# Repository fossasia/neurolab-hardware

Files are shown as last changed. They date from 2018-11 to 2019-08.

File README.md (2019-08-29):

# Neurolab Hardware

Repository for Neurolab Open Hardware platform.






We are developing a neuro-device to collect brainwaves as a headband with integrated electronics. This repository holds the PCB schematics and layouts for the Neurolab Hardware. 

Front Side               | Back Side
 ----------------------- | ---------------------------
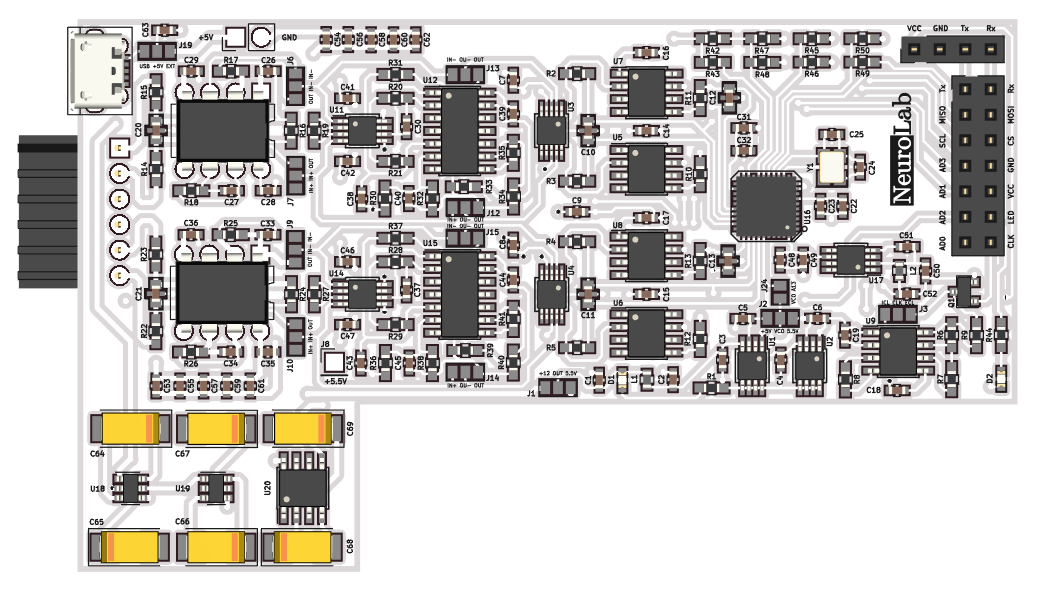
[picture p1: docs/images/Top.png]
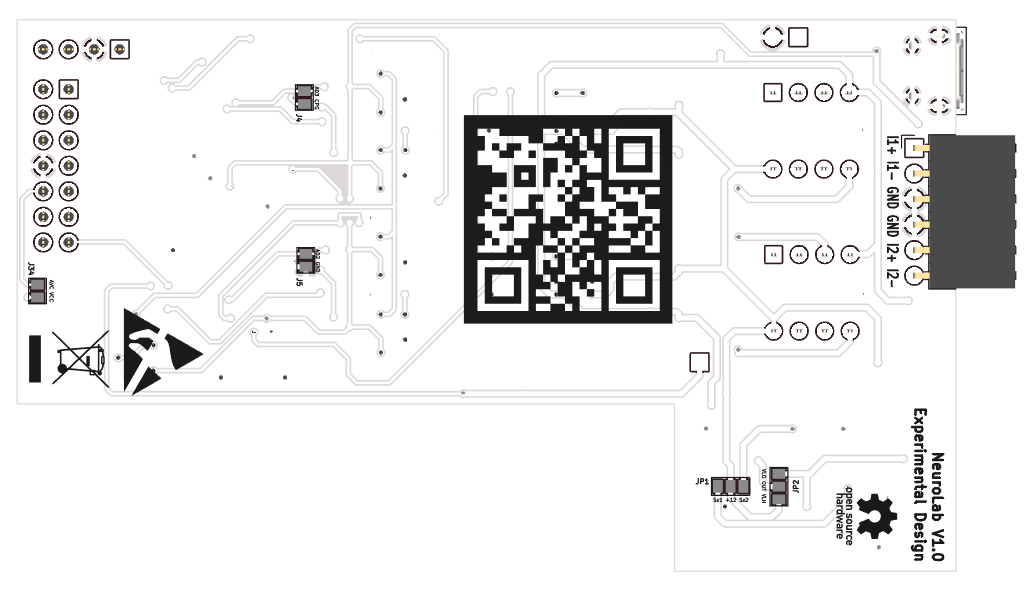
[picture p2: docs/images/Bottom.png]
 | 

## Buy

* You can get the device in future from the [FOSSASIA Shop](https://fossasia.com).
* More resellers will be listed on the [PSLab website](https://pslab.io/shop/).

## Communication

* The Neurolab [chat channel is on Gitter](https://gitter.im/fossasia/neurolab).
* Please also join us on the [Mailing List](https://groups.google.com/forum/#!forum/pslab-fossasia).

## Goal and Roadmap
The goal of the Neurolab project is to develop an easy to use open hardware measurement headset device for brain waves that can be plugged into an Android smartphone and a software application and enables us to understand our brains better.

Our brains communicate through neurotransmitters and their activity emits electricity. The neuroheadset measures that electricity on the skin of the forehead and the software processes the signal so that it can translated into a visual or auditory representation. The data that can be collected can be analysed to identify mental health, stress, relaxation and even diseases like Alzheimer. 

Current devices in the medical industry are usually not accessible by doctors due to their high pricing. They are also complicated to use. The idea of the device is to integrate it into a headband and focus on signals that can be obtained through the frontal lobe.

A difference to existing projects like OpenBCI is that it will not be necessary to 3D print large headsets. Instead we are focusing on creating a device that collects as much data as possible through the forehead. To achieve this goal we are using high-grade sensors and flexible electronics.

## License

This project is licensed under the Apache License 2.0. A copy of [LICENSE](LICENSE) is to be present along with the source code. To obtain the software under a different license, please contact FOSSASIA.

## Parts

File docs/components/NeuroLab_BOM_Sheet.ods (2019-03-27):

# | Description | Mfr. Part Number | Part | References | Value | Footprint | Quantity | Datasheet | Avg Price | Sub Total
1 | Feedthrough Cap 0603 20% 16V | 100X14W104MV4T | C_Feedthrough | C10 C11 C12 C13 | 0.1u | Decouple_Cap_0603 | 4 | https://www.mouser.sg/datasheet/2/611/jdi-x2y-1313433.pdf | $0.302 | $1.21
2 | 16V 10% | 885012206046 | Capacitor | C14 C15 C16 C17 C18 C23 C28 C29 C31 C35 C36 C49 C50 C61 C62 | 0.1u | C_0603 | 15 | https://www.mouser.sg/datasheet/2/445/885012206046-554212.pdf | $0.056 | $0.84
3 | Tantalum 16V 6032-28 | F931C107KCC | CP | C64 C65 C66 C67 C68 C69 | 100u | CP_Tantalum_Case-C_EIA-6032-28_Reflow | 6 | https://www.mouser.com/datasheet/2/40/f93-776559.pdf | $1.230 | $7.38
4 | Feedthrough Cap 0603 20% 50V | 500X14W102MV4T | C_Feedthrough | C20 C21 | 1n | Decouple_Cap_0603 | 2 | https://www.mouser.sg/datasheet/2/611/jdi-x2y-1313433.pdf | $0.342 | $0.68
5 | 16V 10% | 885012206052 | Capacitor | C22 C30 C32 C37 C39 C44 | 1u | C_0603 | 6 | https://www.mouser.sg/datasheet/2/445/885012206052-554330.pdf | $0.059 | $0.35
6 | 16V 10% | CC0603KRX7R7BB222 | Capacitor | C19 | 2.2n | C_0603 | 1 | https://www.mouser.sg/datasheet/2/447/UPY-GPHC_X7R_6.3V-to-50V_18-1154002.pdf | $0.039 | $0.04
7 | 16V 10% | CC0603ZRY5V7BB225 | Capacitor | C1 C2 C3 C4 C7 C8 C9 C41 C42 C46 C47 C48 C51 C52 C53 C54 C55 C56 C57 C58 C59 C60 | 2.2u | C_0603 | 22 | https://www.mouser.sg/datasheet/2/447/UPY-GPHC_Y5V_6.3V-to-50V_8-1280790.pdf | $0.050 | $1.10
8 | 16V 10% | 885012206038 | Capacitor | C26 C27 C33 C34 | 4.7n | C_0603 | 4 | https://www.mouser.sg/datasheet/2/445/885012206038-554208.pdf | $0.021 | $0.08
9 | 16V 10% | C1608X6S1C475K080AC | Capacitor | C5 C6 C63 | 4.7u | C_0603 | 3 | https://www.mouser.sg/datasheet/2/400/lcc_commercial_general_en-837201.pdf | $0.338 | $1.01
10 | 16V 10% | 885012006021 | Capacitor | C38 C40 C43 C45 | 47p | C_0603 | 4 | https://www.mouser.sg/datasheet/2/445/885012006021-553597.pdf | $0.024 | $0.10
11 | 16V 10% | VJ0603A8R2BXJPW1BC | Capacitor | C24 C25 | 8p | C_0603 | 2 | https://www.mouser.sg/datasheet/2/427/vjw1bcbascomseries-223529.pdf | $0.140 | $0.28
12 | Green 0805 | Green 0805 | SMD LED | D1 | Green | LED_0603 | 1 | - | -
13 | Blue 0805 | Blue 0805 | SMD LED | D2 | Blue | LED_0603 | 1 | - | -
14 | Straight female 2.54 mm 1row | SSW-101-01-T-S | Conn_01x01 | J8 | 5.5V | Pin_Header_Straight_1x01_Pitch2.54mm | 1 | - | -
15 | Straight female 2.54 mm 1row | SSW-104-01-T-S | Conn_01x04 | J32 | Bluetooth | Pin_Header_Straight_1x04_Pitch2.54mm | 1 | - | -
16 | Straight female 2.54 mm 1row | SSW-106-01-T-S | Conn_01x06 | J16 | Channel | Pin_Header_Angled_1x06_Pitch2.54mm | 1 | - | -
17 | Straight female 2.54 mm 1row | SSW-102-01-T-S | Conn_01x02 | J17 | External | Pin_Header_Straight_1x02_Pitch2.54mm | 1 | - | -
18 | Straight female 2.54 mm 2row | SSW-107-01-T-D | Conn_02x07 | J11 | ProMini | Pin_Header_Straight_2x07_Pitch2.54mm | 1 | - | -
19 | USB SMT+DIP Type | ZX62D-B-5PA8(30) | USB_OTG | J18 | USB_OTG | USB_Micro-B | 1 | https://www.mouser.sg/datasheet/2/185/ZX_catalog-939768.pdf | $1.050 | $1.05
20 | Ferrite Bead | BK1608LL121-T | Inductor | L1 L2 | BLM15HB121SN1 | L_0603 | 2 | https://www.mouser.sg/datasheet/2/396/mlci07_e-1396618.pdf | $0.100 | $0.20
21 | SOT 23-3 N-MOSFET | 2N7002 | 2N7002 | Q1 | 2N7002 | SOT-23 | 1 | https://www.mouser.sg/datasheet/2/308/2N7002-1305074.pdf | $0.330 | $0.33
22 | 1/16W 20% | RR0816P-104-D | Chip Resistor | R7 R17 R18 R25 R26 R34 R35 R40 R41 | 100k | R_0603_HandSoldering | 9 | - | $0.050 | $0.45
23 | 1/16W 20% | RR0816P-103-D | Chip Resistor | R8 R9 R42 R43 | 10k | R_0603_HandSoldering | 4 | - | $0.050 | $0.20
24 | 1/16W 20% | RR1220P-105-D | Chip Resistor | R20 R28 R31 R32 R33 R37 R38 R39 | 1M | R_0603_HandSoldering | 8 | - | $0.085 | $0.68
25 | 1/16W 20% | RR0816P-102-D | Chip Resistor | R6 R46 R47 R49 | 1k | R_0603_HandSoldering | 4 | - | $0.050 | $0.20
26 | 1/16W 20% | RC0603JR-07200RL | Chip Resistor | R19 R27 | 200 | R_0603_HandSoldering | 2 | - | $0.050 | $0.10
27 | 1/16W 20% | RC0603JR-0720KL | Chip Resistor | R1 | 20k | R_0603_HandSoldering | 1 | - | $0.100 | $0.10
28 | 1/16W 20% | RT0603FRE072KL | Chip Resistor | R16 R24 R45 R48 R50 | 2k | R_0603_HandSoldering | 5 | - | $0.085 | $0.43
29 | 1/16W 20% | RC0603FR-074K02L | Chip Resistor | R21 R29 R30 R36 | 4.02k | R_0603_HandSoldering | 4 | - | $0.085 | $0.34
30 | 1/16W 20% | RR0816P-472-D | Chip Resistor | R2 R3 R4 R5 R14 R15 R22 R23 | 4.7k | R_0603_HandSoldering | 8 | - | $0.085 | $0.68
31 | 1/16W 20% | RR0816P-471-D | Chip Resistor | R10 R11 R12 R13 | 470 | R_0603_HandSoldering | 4 | - | $0.085 | $0.34
32 | 1/16W 20% | RR0816P-512-D | Chip Resistor | R44 | 5.1k | R_0603_HandSoldering | 1 | - | $0.100 | $0.10
33 | SOIC 8 Voltage Inverter | TC7660SEOA713 | TC7660 | U20 | TC7660 | SOIC-8_3.9x4.9mm_Pitch1.27mm | 1 | https://www.mouser.sg/datasheet/2/268/21467B-1180369.pdf | $0.920 | $0.92
34 | 24bit ADC QFN24 EP LFCSP-40 | AD7173-8BCPZ | AD7173 | U16 | AD7173 | LFCSP-40-1EP | 1 | https://www.mouser.sg/datasheet/2/609/AD7173-8-877372.pdf | $16.690 | $16.69
35 | Instumentation Amplifier | AD8220BRMZ | AD8220 | U11 U14 | AD8422ARMZ | MSOP-8_3x3mm_Pitch0.65mm | 2 | https://www.mouser.sg/datasheet/2/609/AD8220-877764.pdf | $8.813 | $17.63
36 | Diff Amp MOSP 10 | AD8475ARMZ | AD8475 | U3 U4 | AD8475 | MSOP-10_3x3mm_Pitch0.5mm | 2 | https://www.mouser.sg/datasheet/2/609/AD8475-1502173.pdf | $4.915 | $9.83
37 | LDO Regulator MSOP 8 | ADP1720ARMZ-3.3-R7 | ADP1720ARMZ-3.3 | U2 | ADP1720ARMZ-3.3 | MSOP-8_3x3mm_Pitch0.65mm | 1 | https://www.mouser.sg/datasheet/2/609/ADP1720-1503421.pdf | $1.790 | $1.79
38 | LDO Regulator MSOP 8 | ADP1720ARMZ-5-R7 | ADP1720ARMZ-5 | U1 | ADP1720ARMZ-5 | MSOP-8_3x3mm_Pitch0.65mm | 1 | https://www.mouser.sg/datasheet/2/609/ADP1720-1503421.pdf | $1.790 | $1.79
39 | MSOP 8 Voltage Reference | ADR445ARMZ | ADR445BR | U17 | ADR445BR | MSOP-8_3x3mm_Pitch0.65mm | 1 | https://www.mouser.sg/datasheet/2/609/adr440_441_443_444_445-1529927.pdf | $5.846 | $5.85
40 | SOIC 8 8th-Order Lowpass Butterworth | MAX7480ESA+ | MAX7480ESA+ | U5 U6 U7 U8 | MAX7480ESA+ | SOIC-8_3.9x4.9mm_Pitch1.27mm | 4 | https://www.mouser.sg/datasheet/2/256/MAX7480-1515905.pdf | $4.150 | $16.60
41 | SOIC 14 Precision Amplifier | OP4177ARZ | OP4177 | U12 U15 | OP4177 | SOIC-14_3.9x8.7mm_Pitch1.27mm | 2 | https://www.mouser.sg/datasheet/2/609/OP1177_2177_4177-879575.pdf | $7.860 | $15.72
42 | DIP 8 Low Noise Differential Amplifier | OPA2111KP | OPA2111KP | U10 U13 | OPA2111KP | DIP-8_W7.62mm | 2 | http://www.ti.com/general/docs/suppproductinfo.tsp?distId=26 | $20.510 | $41.02
43 | SOT 23-6 Voltage Doubler | TC1240AECHTR | TC1240A | U18 U19 | TC1240A | SOT-23-6 | 2 | https://www.mouser.sg/datasheet/2/268/21516c-4387.pdf | $0.840 | $1.68
44 | SOIC 8 555 Timer | TLC555CDR | TLC555CD | U9 | TLC555CD | SOIC-8_3.9x4.9mm_Pitch1.27mm | 1 | http://www.ti.com/general/docs/suppproductinfo.tsp?distId=26 | $0.730 | $0.73
45 | Crystals 16MHz 50PPM -20C +70C 18.0pF | FA-238 16.0000MB-C3 | Crystal_GND24_Small | Y1 | FA-20H | Crystal_SMD_SeikoEpson_FA238-4pin_3.2x2.5mm | 1 | https://www.mouser.sg/datasheet/2/137/A-238_en-932914.pdf | $0.340 | $0.34
46 | EEG Dry electrodes |  |  |  |  |  | 4 |  |  | $148.86
47 | EEG electrode casing |  |  |  |  |  | 4
 | Component Groups: |  | 45
 | Component Count: |  | 151
 | Fitted Components: |  | 151
 | Number of PCBs: |  | 1
 | Total components: |  | 151
 | Schematic Version: |  | v1
 | Revised |  | 09th March 2019

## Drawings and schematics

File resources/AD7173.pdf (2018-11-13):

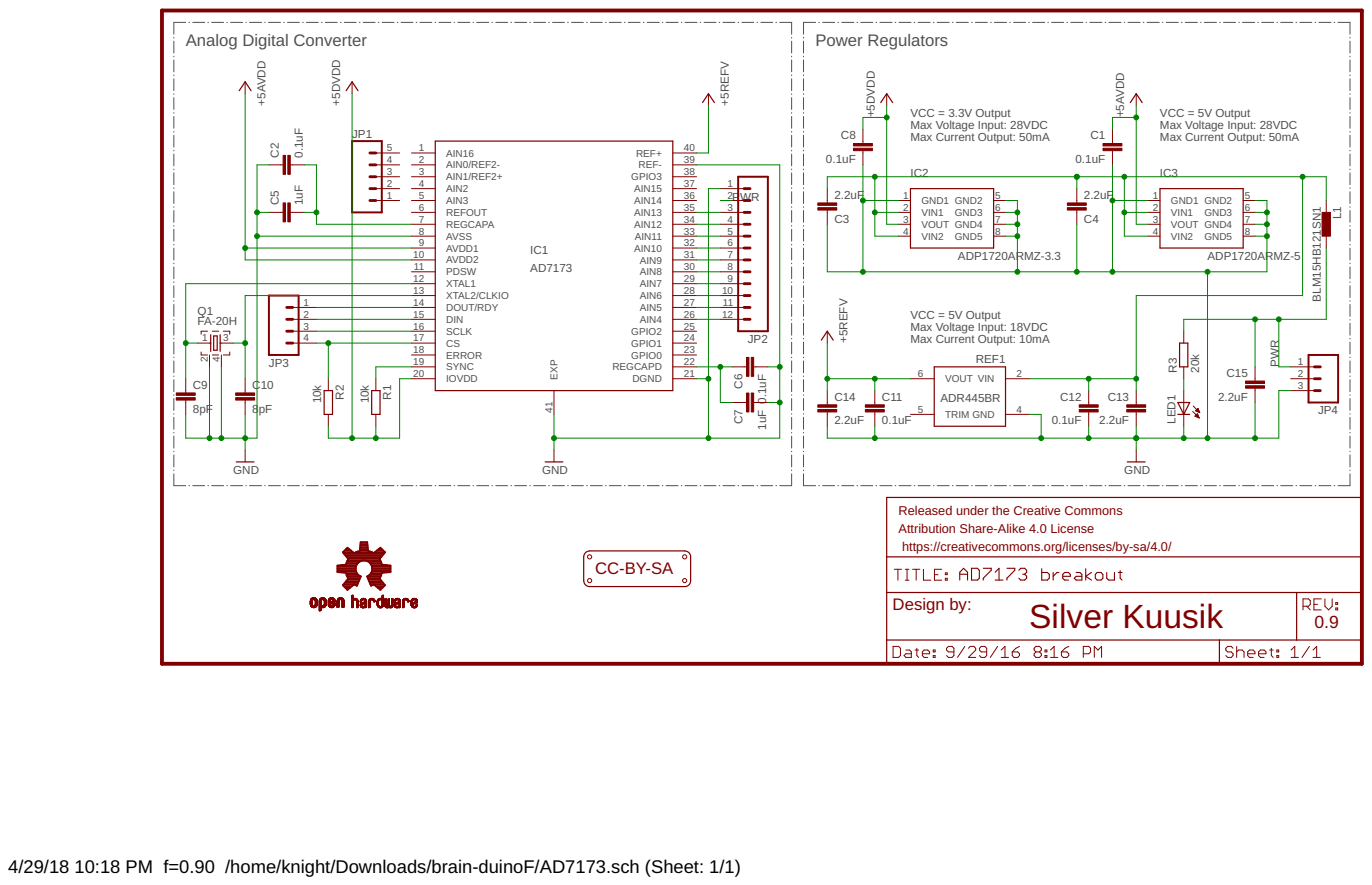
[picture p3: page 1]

VCC = 3.3V Output Max Current Output: 50mA Max Voltage Input: 28VDC

VCC = 5V Output Max Current Output: 50mA Max Voltage Input: 28VDC

VCC = 5V Output Max Voltage Input: 18VDC Max Current Output: 10mA

Released under the Creative Commons Attribution Share-Alike 4.0 License

https://creativecommons.org/licenses/by-sa/4.0/

4/29/18 10:18 PM f=0.90 /home/knight/Downloads/brain-duinoF/AD7173.sch (Sheet: 1/1)

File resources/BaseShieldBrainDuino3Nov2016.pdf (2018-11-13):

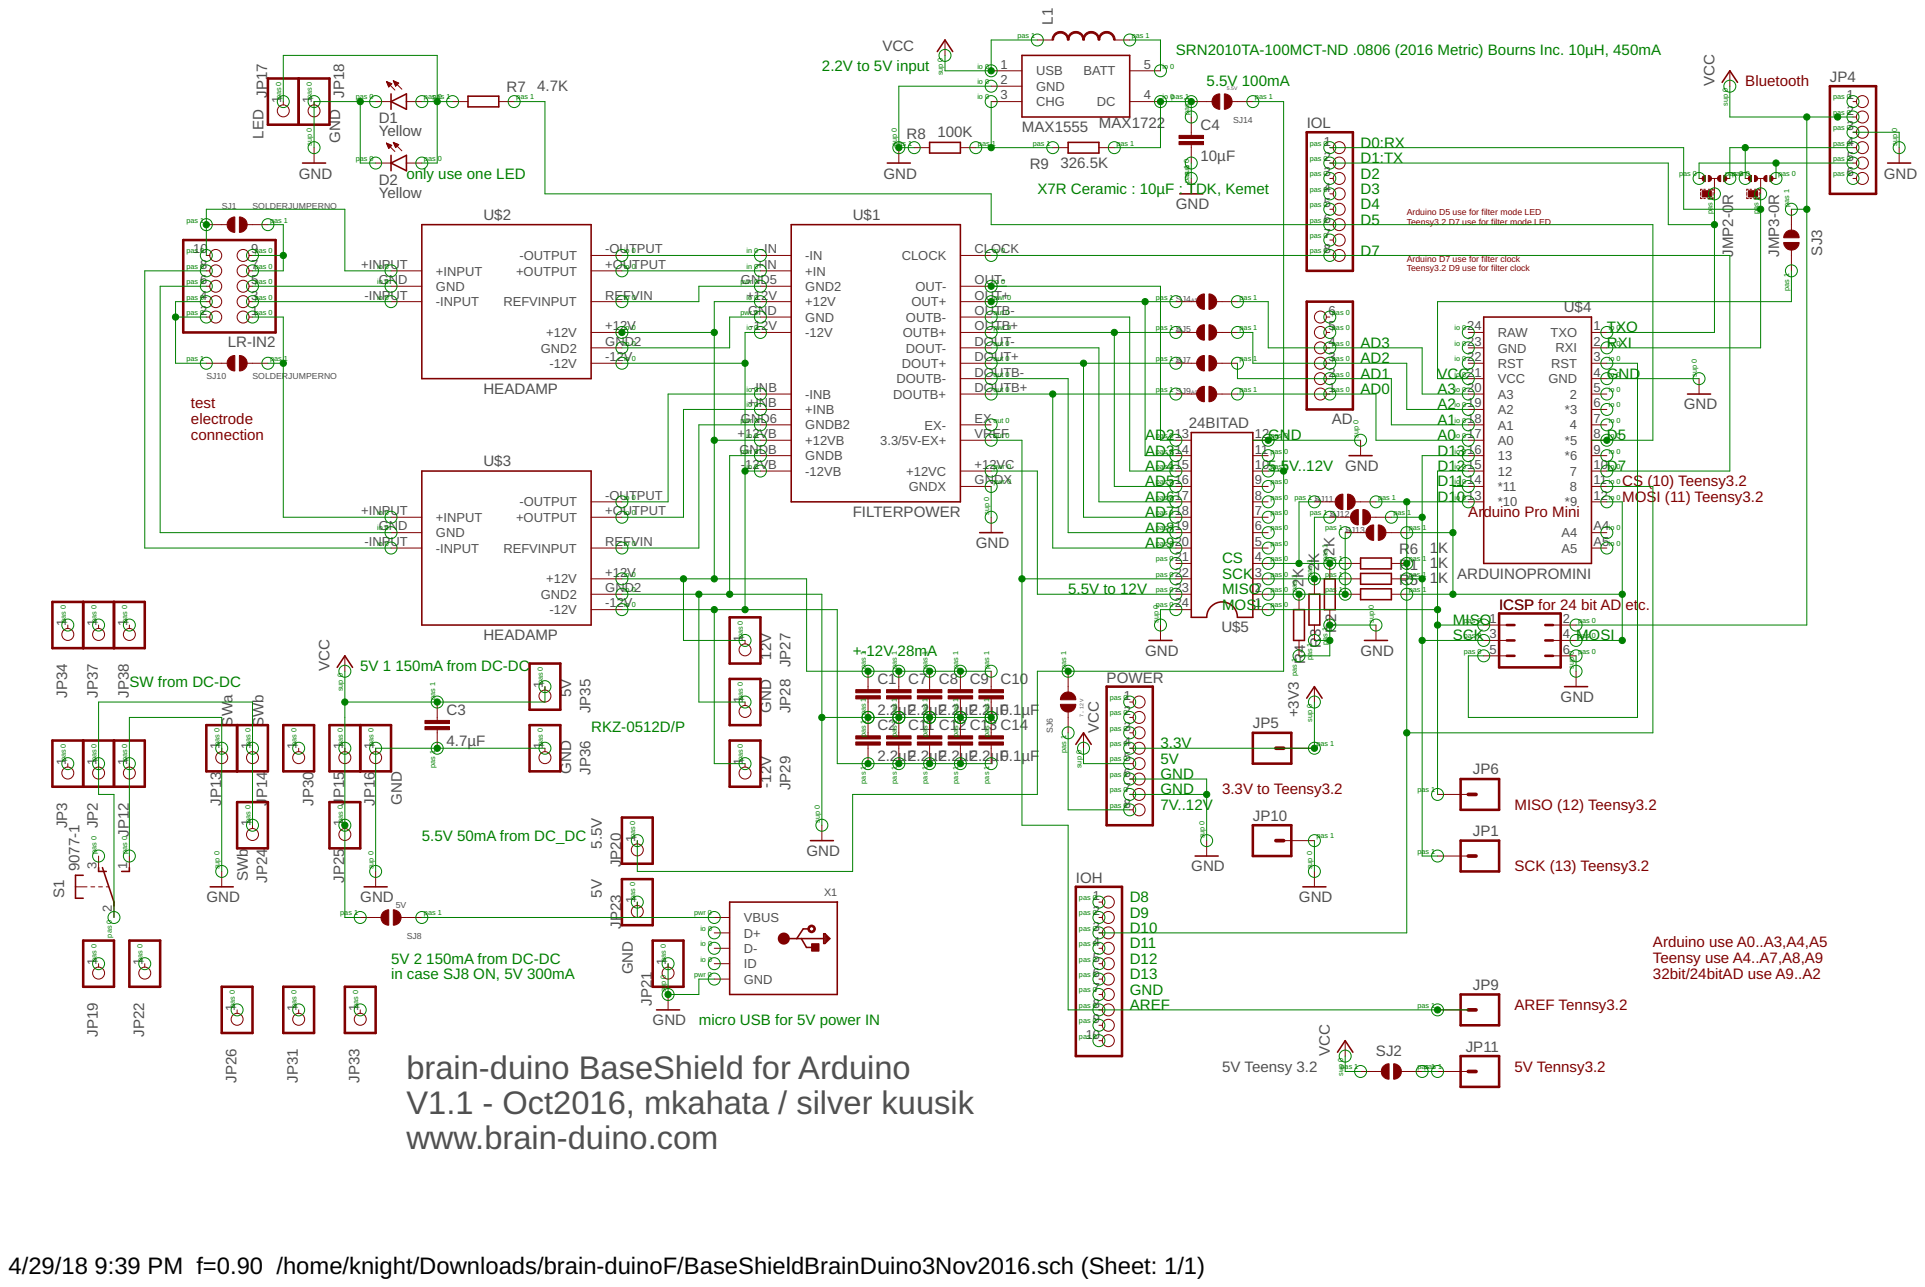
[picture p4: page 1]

SRN2010TA-100MCT-ND .0806 (2016 Metric) Bourns Inc. 10µH, 450mA

only use one LED

Arduino D5 use for filter mode LED
Teensy3.2 D7 use for filter mode LED

Arduino D7 use for filter clock Teensy3.2 D9 use for filter clock

ICSP for 24 bit AD etc.

VCC brain-duino BaseShield for Arduino
5V 1 150mA from DC-DC

SCK 3 pas 0 | | 4 pas 0

pas 1 pas 1

SW from DC-DC

Arduino use A0..A3,A4,A5 Teensy use A4..A7,A8,A9

V1.1 - Oct2016, mkahata / silver kuusik
www.brain-duino.com

4/29/18 9:39 PM f=0.90 /home/knight/Downloads/brain-duinoF/BaseShieldBrainDuino3Nov2016.sch (Sheet: 1/1)

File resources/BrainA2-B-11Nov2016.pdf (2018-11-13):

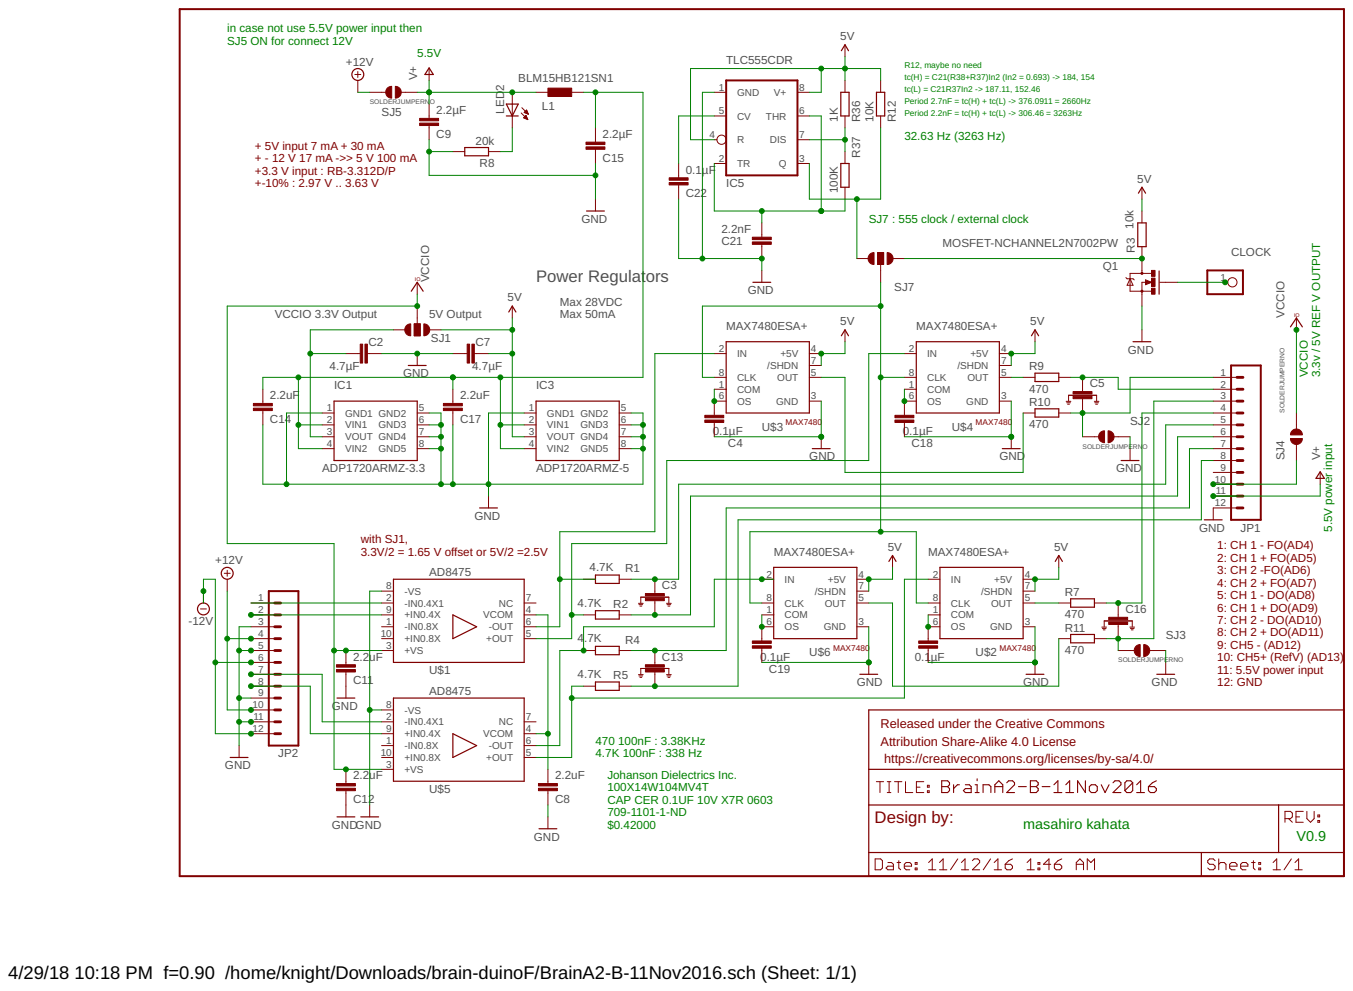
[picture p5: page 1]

in case not use 5.5V power input then SJ5 ON for connect 12V

R12, maybe no need
tc(L) = C21R37In2 -> 187.11, 152.46 Period 2.7nF = tc(H) + tc(L) -> 376.0911 = 2660Hz Period 2.2nF = tc(H) + tc(L) -> 306.46 = 3263Hz

9: CH5 - (AD12) 10: CH5+ (RefV) (AD13) 11: 5.5V power input 12: GND

MAX7480 Released under the Creative Commons Attribution Share-Alike 4.0 License

https://creativecommons.org/licenses/by-sa/4.0/

Johanson Dielectrics Inc. 100X14W104MV4T CAP CER 0.1UF 10V X7R 0603

4/29/18 10:18 PM f=0.90 /home/knight/Downloads/brain-duinoF/BrainA2-B-11Nov2016.sch (Sheet: 1/1)

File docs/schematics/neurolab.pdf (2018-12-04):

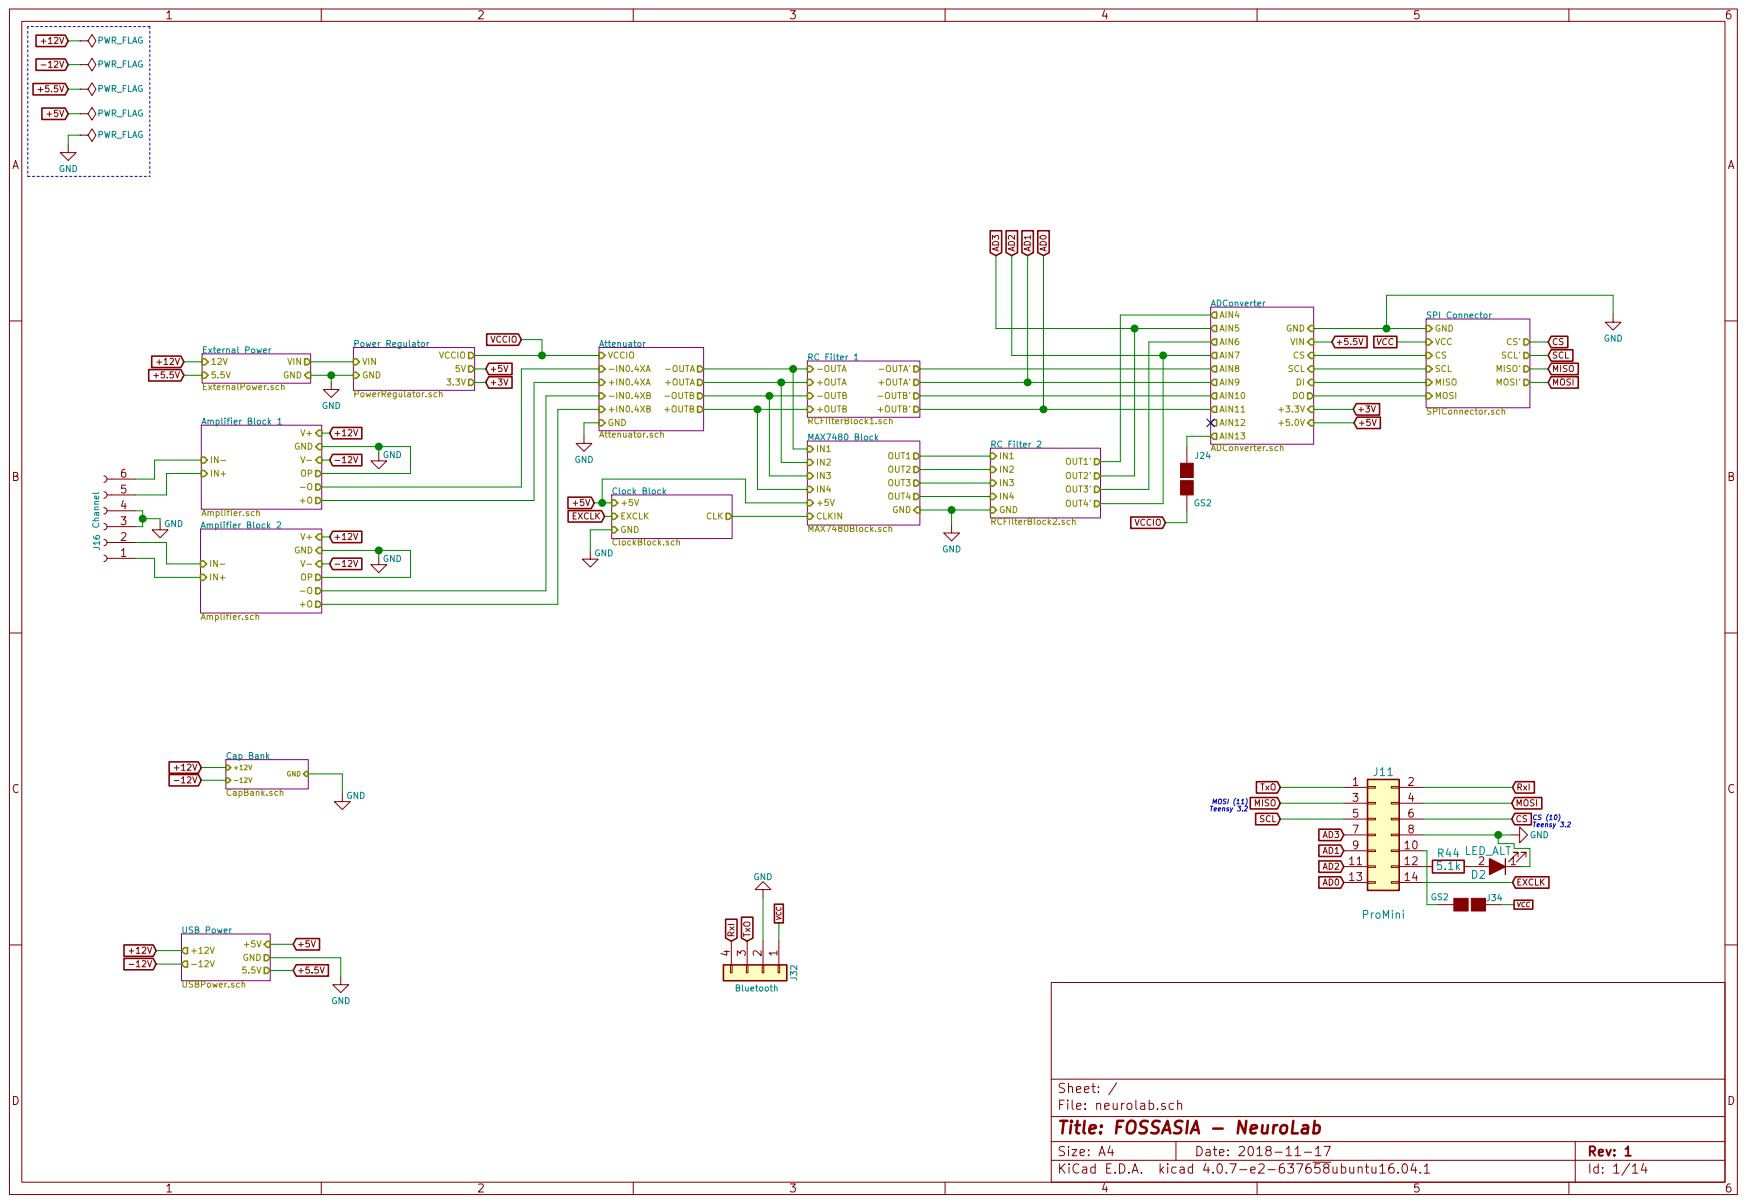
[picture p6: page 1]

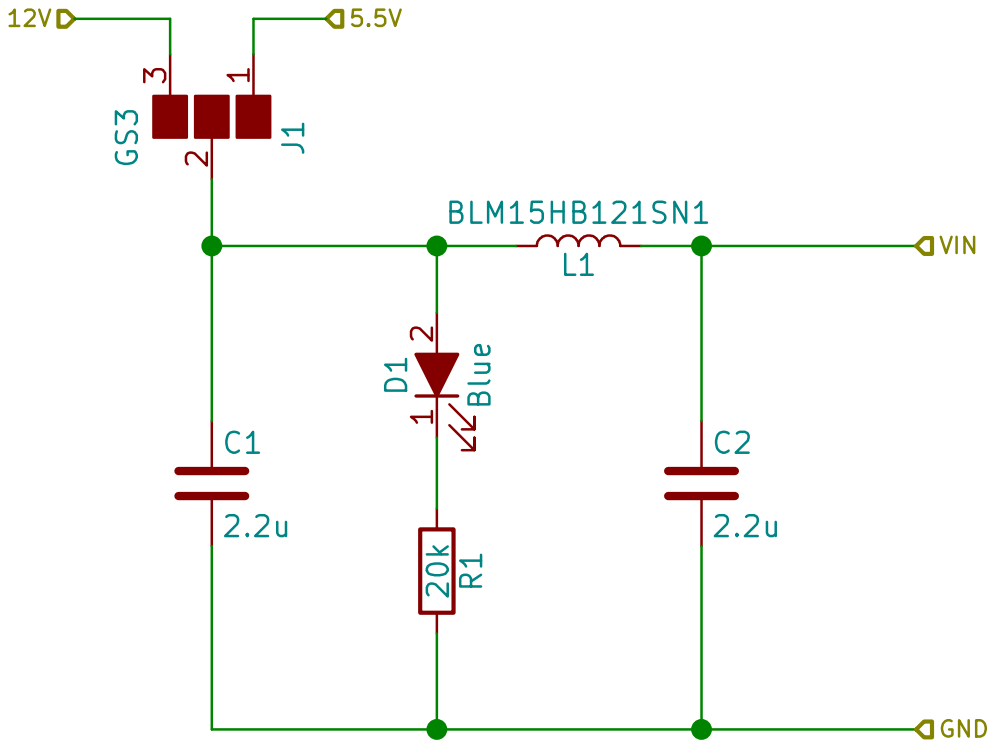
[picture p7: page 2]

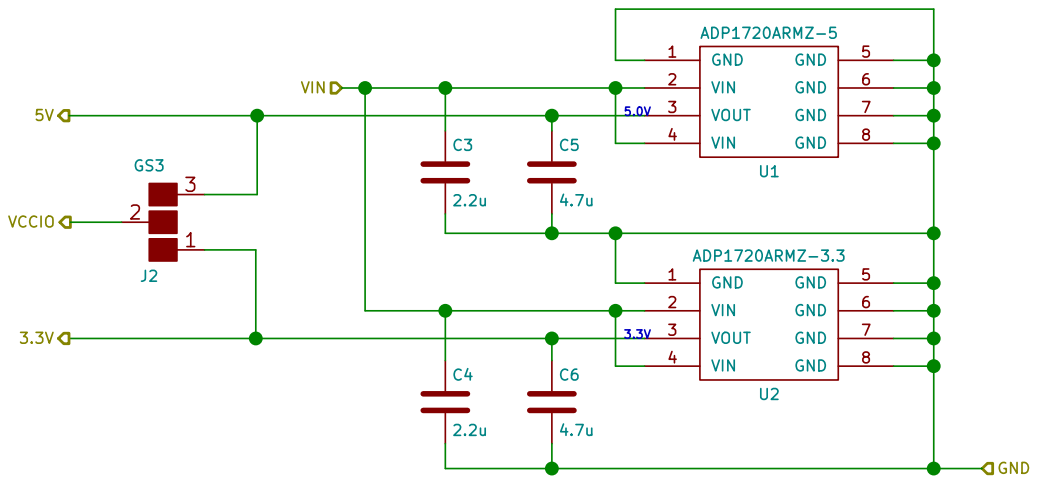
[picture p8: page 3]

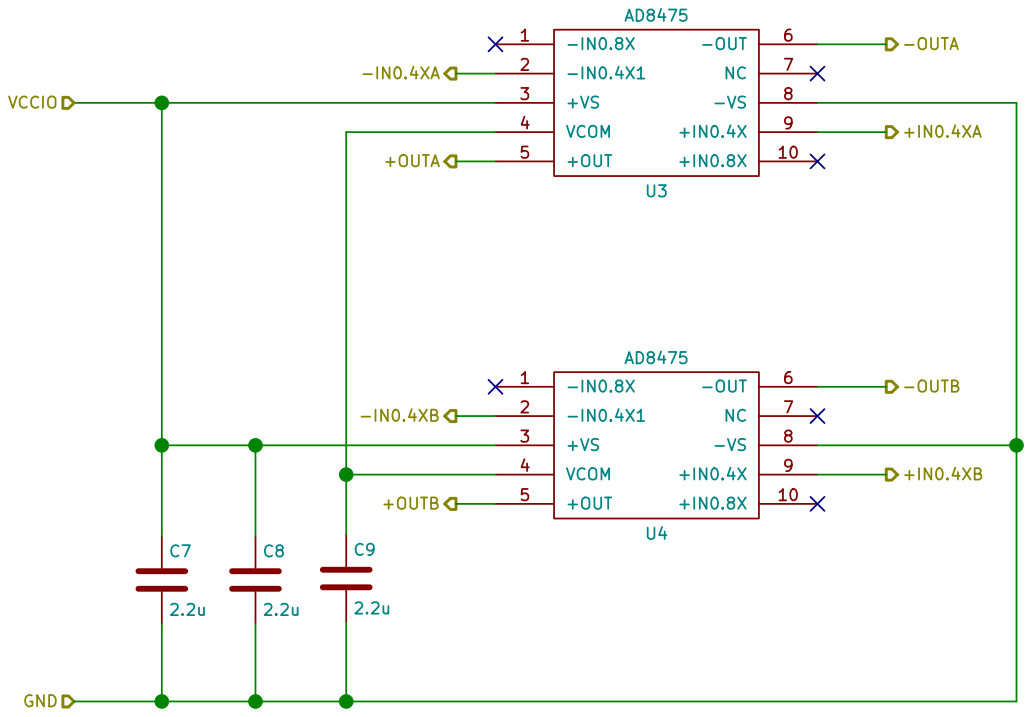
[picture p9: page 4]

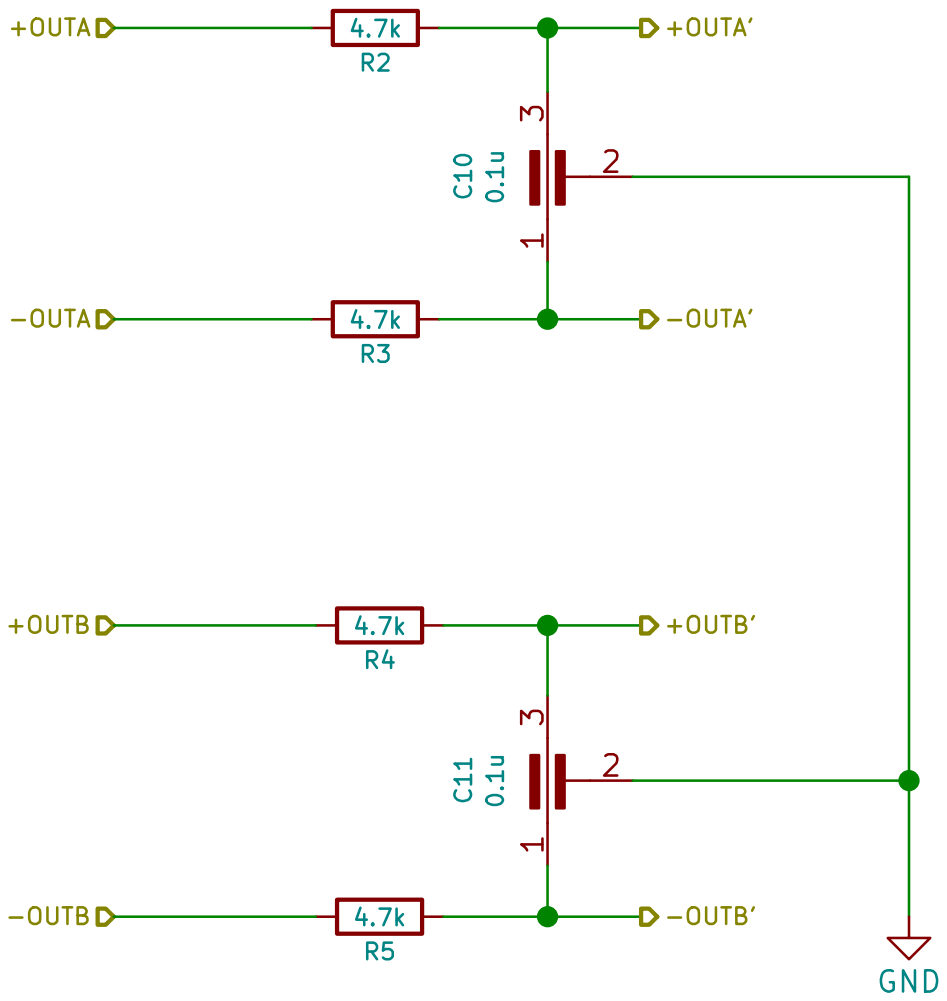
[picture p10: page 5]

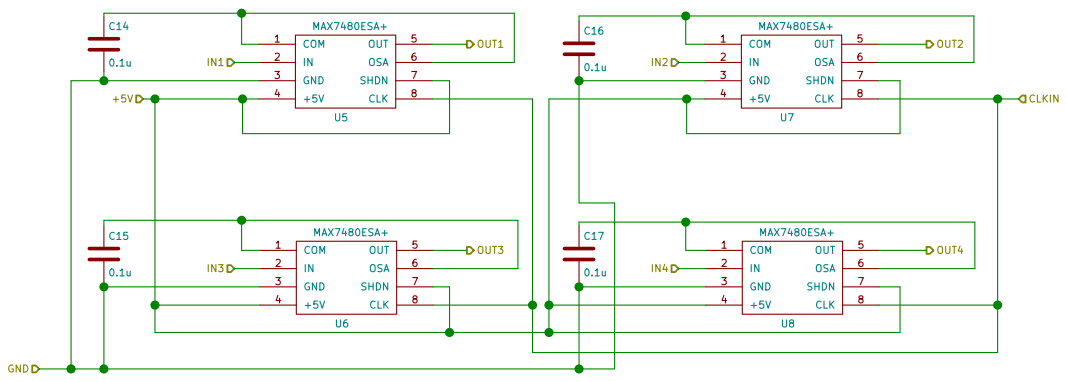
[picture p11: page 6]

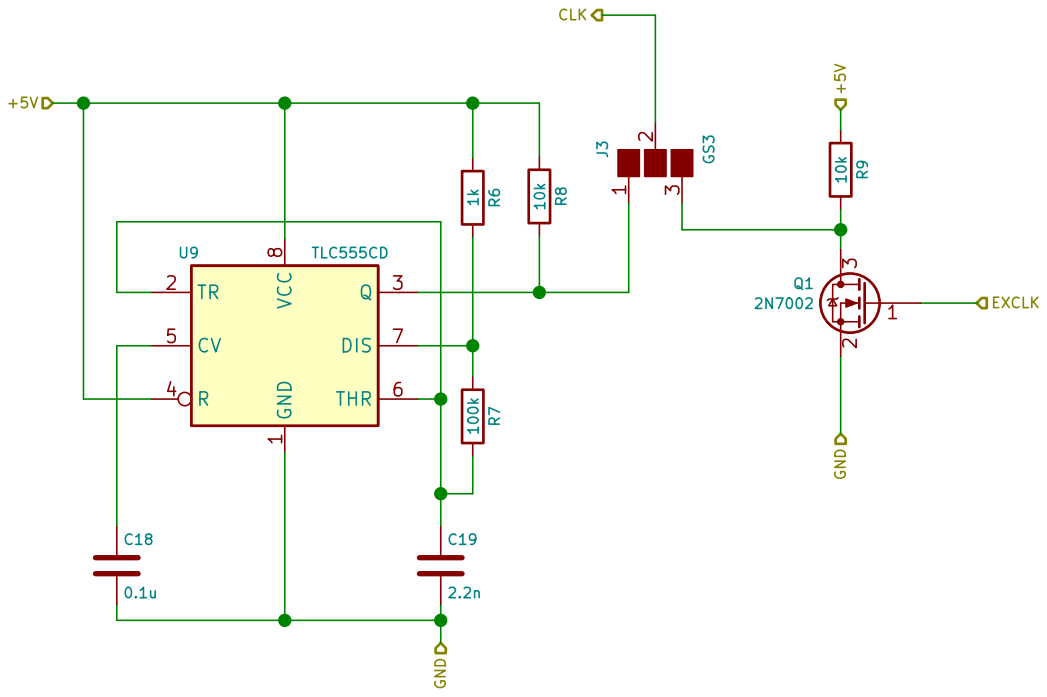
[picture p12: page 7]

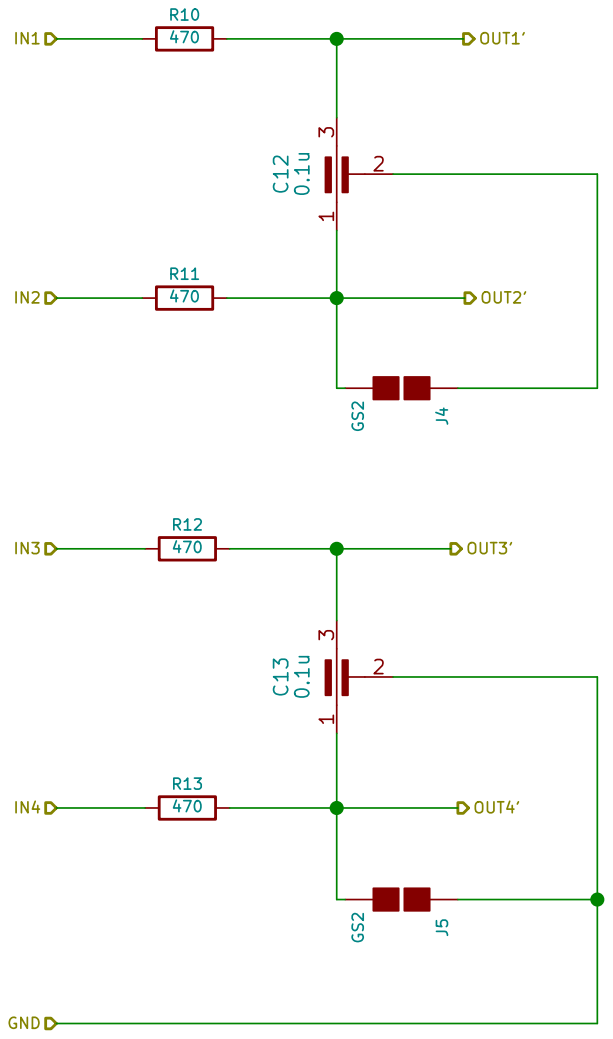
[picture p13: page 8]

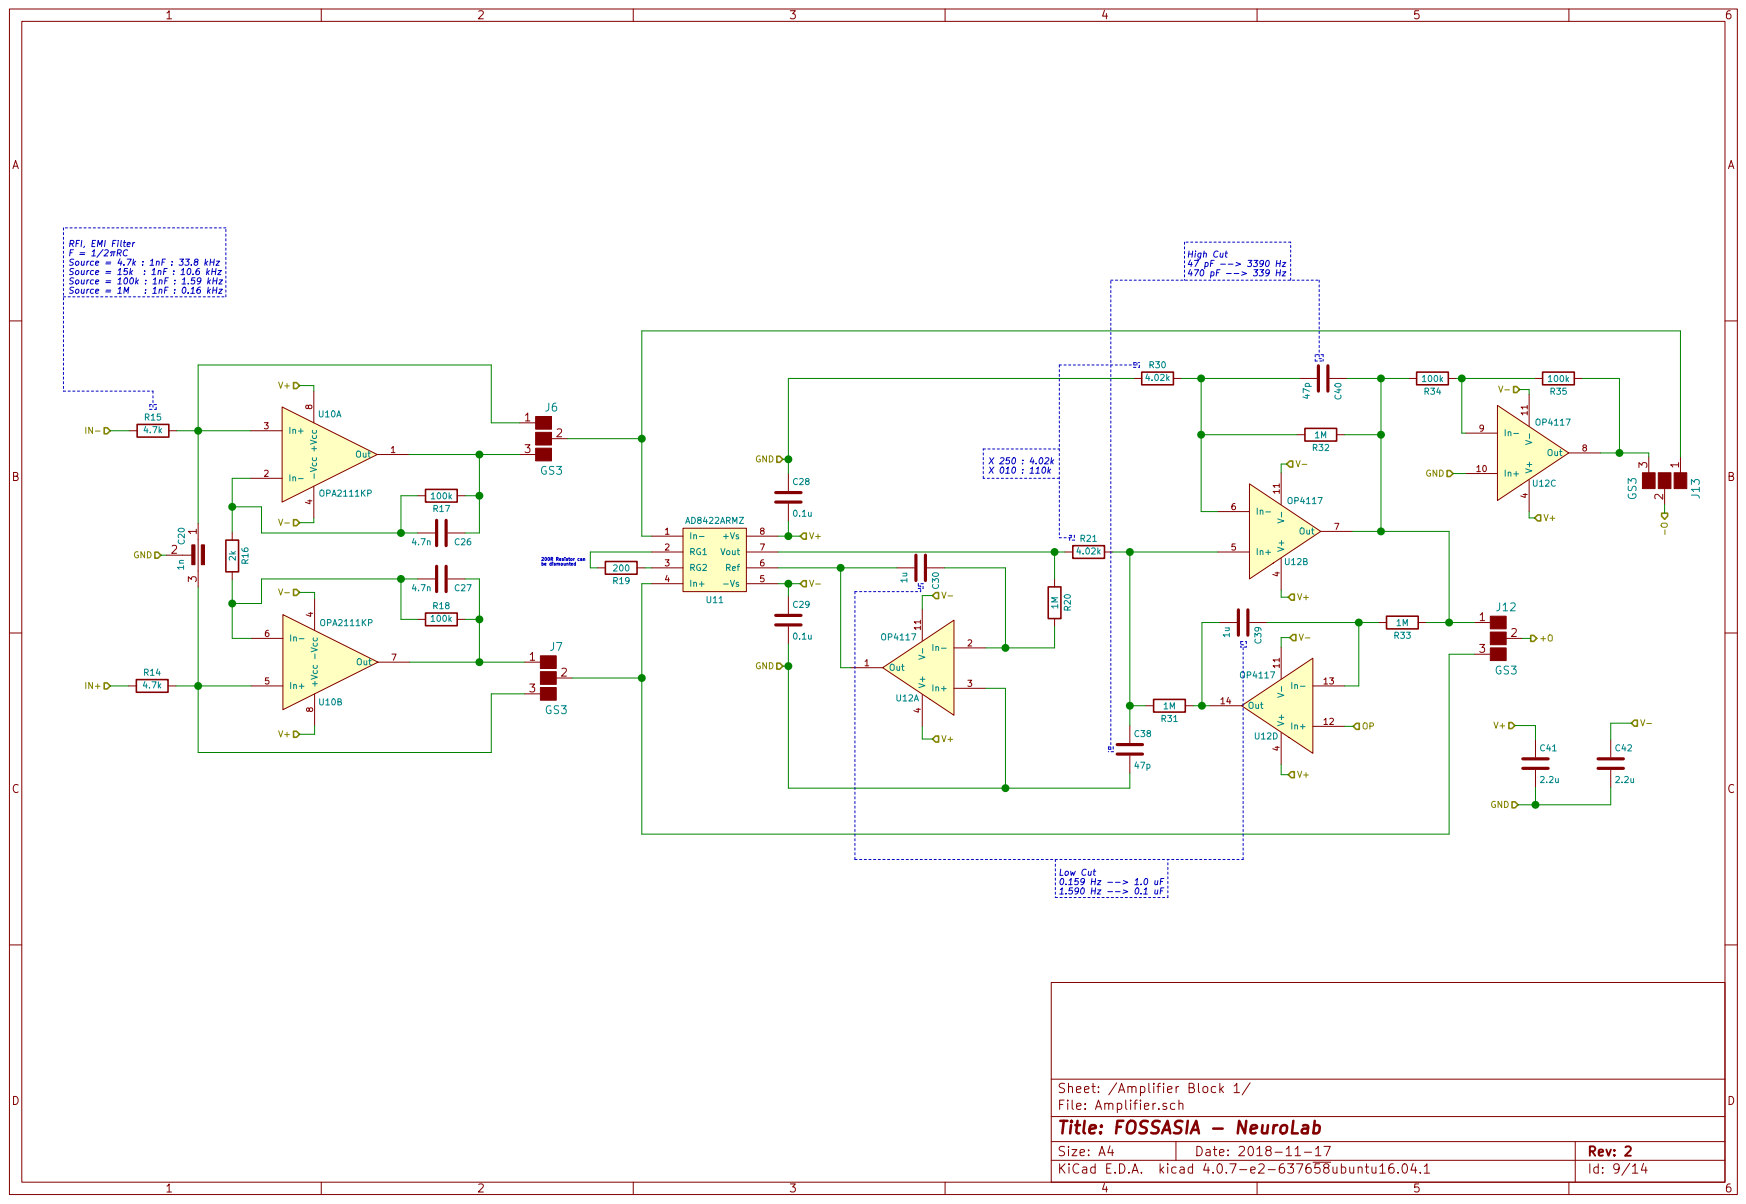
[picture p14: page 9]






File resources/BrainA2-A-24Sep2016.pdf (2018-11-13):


4/29/18 10:19 PM /home/knight/Downloads/brain-duinoF/BrainA2-A-24Sep2016.sch (Sheet: 1/1)

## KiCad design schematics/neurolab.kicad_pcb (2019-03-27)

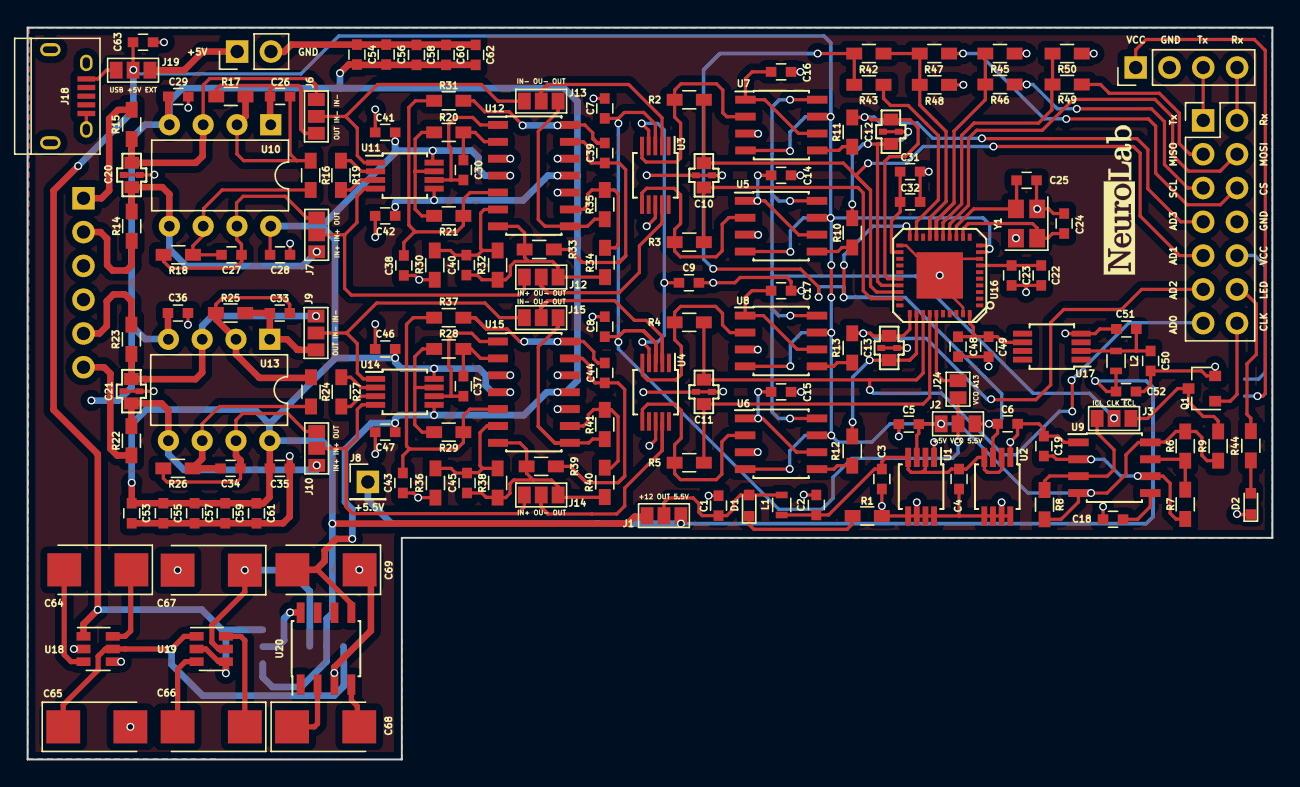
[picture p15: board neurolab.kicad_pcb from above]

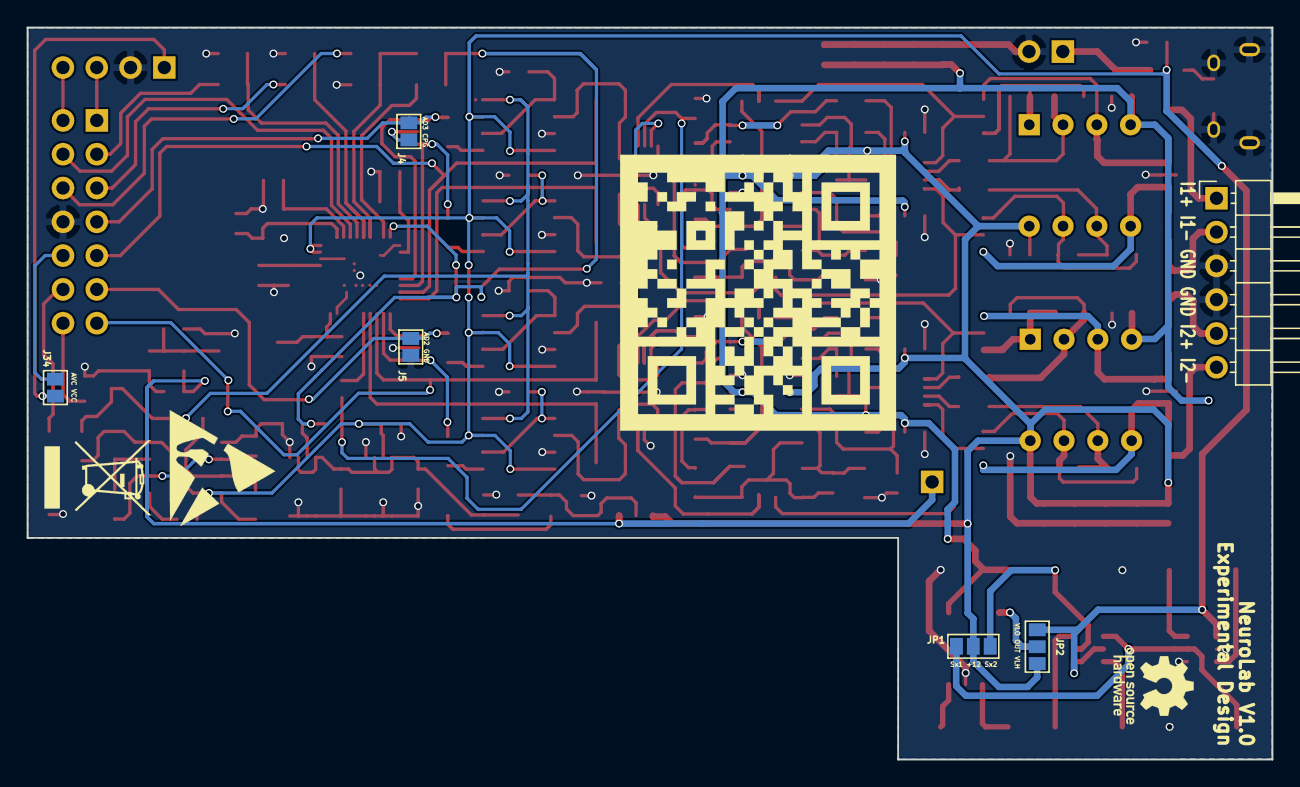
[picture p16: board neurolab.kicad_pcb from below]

Board: 2 copper layers, 93.6 x 55.0 mm, 169 parts (6 on the bottom side), 119 nets.

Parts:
C1, C2, C3, C4, C7, C8, C9, C41, C42, C46, C47, C48, C51, C52, C53, C54, C55, C56, C57, C58, C59, C60: 2.2u; C_0603
C5, C6, C63: 4.7u; C_0603
C10, C11, C12, C13: 0.1u; Decouple_Cap_0603
C14, C15, C16, C17, C18, C23, C28, C29, C31, C35, C36, C49, C50, C61, C62: 0.1u; C_0603
C19: 2.2n; C_0603
C20, C21: 1n; Decouple_Cap_0603
C22, C30, C32, C37, C39, C44: 1u; C_0603
C24, C25: 8pF; C_0603
C26, C27, C33, C34: 4.7n; C_0603
C38, C40, C43, C45: 47p; C_0603
C64, C65, C66, C67, C68, C69: 100u; CP_Tantalum_Case-C_EIA-6032-28_Reflow
D1: Blue; LED_0603
D2: LED_ALT; LED_0603
J1, J2, J3, J6, J7, J9, J10, J12, J13, J14, J15, J19: GS3
J4, J5, J24, J34: GS2
J8: 5.5V; Pin_Header_Straight_1x01_Pitch2.54mm
J11: ProMini; Pin_Header_Straight_2x07_Pitch2.54mm
J16: Channel; Pin_Header_Angled_1x06_Pitch2.54mm
J17: External; Pin_Header_Straight_1x02_Pitch2.54mm
J18: USB_OTG; USB_Micro-B
J32: Bluetooth; Pin_Header_Straight_1x04_Pitch2.54mm
JP1: VoltOut; GS3
JP2: VVV; GS3
L1, L2: BLM15HB121SN1; L_0603
Q1: 2N7002; SOT-23
R1: 20k; R_0603_HandSoldering
R2, R3, R4, R5, R14, R15, R22, R23: 4.7k; R_0603_HandSoldering
R6, R46, R47, R49: 1k; R_0603_HandSoldering
R7, R17, R18, R25, R26, R34, R35, R40, R41: 100k; R_0603_HandSoldering
R8, R9, R42, R43: 10k; R_0603_HandSoldering
R10, R11, R12, R13: 470; R_0603_HandSoldering
R16, R24, R45, R48, R50: 2k; R_0603_HandSoldering
R19, R27: 200; R_0603_HandSoldering
R20, R28, R31, R32, R33, R37, R38, R39: 1M; R_0603_HandSoldering
R21, R29, R30, R36: 4.02k; R_0603_HandSoldering
R44: 5.1k; R_0603_HandSoldering
U1: ADP1720ARMZ-5; MSOP-8_3x3mm_Pitch0.65mm
U2: ADP1720ARMZ-3.3; MSOP-8_3x3mm_Pitch0.65mm
U3, U4: AD8475; MSOP-10_3x3mm_Pitch0.5mm
U5, U6, U7, U8: MAX7480ESA+; SOIC-8_3.9x4.9mm_Pitch1.27mm
U9: TLC555CD; SOIC-8_3.9x4.9mm_Pitch1.27mm
U10, U13: OPA2111KP; DIP-8_W7.62mm
U11, U14: AD8422ARMZ; MSOP-8_3x3mm_Pitch0.65mm
U12, U15: OP4117; SOIC-14_3.9x8.7mm_Pitch1.27mm
U16: AD7173; LFCSP-40-1EP
U17: ADR445BR; MSOP-8_3x3mm_Pitch0.65mm
U18, U19: TC1240A; SOT-23-6
U20: 7660; SOIC-8_3.9x4.9mm_Pitch1.27mm
Y1: FA-20H; Crystal_SMD_SeikoEpson_FA238-4pin_3.2x2.5mm

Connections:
+3V: C6.1, J2.1, R42.2, R43.2, U2.3, U16.20
+5.5V: C52.1, J1.1, J8.1, L2.2
+5V: C5.1, C63.1, J2.3, J19.2, JP2.3, R6.1, R8.1, R9.1, U1.3, U5.4, U5.7, U6.4, U6.7, U7.4, U7.7, U8.4, U8.7, U9.4, U9.8, U16.9, U16.10, U18.1, U19.2, U19.4
+12V: C28.2, C35.2, C41.1, C46.1, C53.1, C55.1, C57.1, C59.1, C61.1, J1.3, JP1.2, JP2.1, U10.8, U11.8, U12.4, U13.8, U14.8, U15.4
-12V: C29.1, C36.1, C42.1, C47.1, C54.2, C56.2, C58.2, C60.2, C62.2, C69.2, U10.4, U11.5, U12.11, U13.4, U14.5, U15.11, U20.5
/ADConverter/AIN4: C12.3, R10.2, U16.27
/ADConverter/AIN6: C13.3, R12.2, U16.32
/ADConverter/AIN13: J24.1, U16.35
/ADConverter/CS: R42.1, R47.2, R48.1, U16.17
/ADConverter/DI: R49.2, R50.1, U16.15
/ADConverter/SCL: R45.1, R46.2, U16.16
/Amplifier Block 1/IN+: J16.2, R14.1
/Amplifier Block 1/IN-: J16.1, R15.1
/Amplifier Block 2/IN+: J16.6, R22.1
/Amplifier Block 2/IN-: J16.5, R23.1
/Attenuator/+IN0.4XA: J12.2, U3.9
/Attenuator/+IN0.4XB: J14.2, U4.9
/Attenuator/+OUTA: R2.2, U3.5, U7.2
/Attenuator/+OUTB: R4.2, U4.5, U8.2
/Attenuator/-IN0.4XA: J13.2, U3.2
/Attenuator/-IN0.4XB: J15.2, U4.2
/Attenuator/-OUTA: R3.2, U3.6, U5.2
/Attenuator/-OUTB: R5.2, U4.6, U6.2
/Clock Block/CLK: J3.2, U5.8, U6.8, U7.8, U8.8
/External Power/VIN: C2.1, C3.1, C4.1, L1.2, U1.2, U1.4, U2.2, U2.4
/RC Filter 1/-OUTA': C10.1, R3.1, U16.29
/RC Filter 1/-OUTB': C11.1, R5.1, U16.34
/RC Filter 2/IN1: R10.1, U5.5
/RC Filter 2/IN2: R11.1, U7.5
/RC Filter 2/IN3: R12.1, U6.5
/RC Filter 2/IN4: R13.1, U8.5
AD0: C11.3, J11.13, R4.1, U16.33
AD1: C10.3, J11.9, R2.1, U16.28
AD2: C13.1, J5.2, J11.11, R13.2, U16.31
AD3: C12.1, J4.2, J11.7, R11.2, U16.26
CS: J11.6, R47.1
EXCLK: J11.14, Q1.1
GND: C1.2, C2.2, C3.2, C4.2, C5.2, C6.2, C7.2, C8.2, C9.2, C10.2, C11.2, C13.2, C14.2, C15.2, C16.2, C17.2, C18.2, C19.2, C20.2, C21.2, C22.2, C23.2, C24.2, C25.2, C28.1, C29.2, C31.2, C32.2, C35.1, C36.2, C38.2, C41.2, C42.2, C43.2, C46.2, C47.2, C48.2, C49.2, C50.2, C51.2, C52.2, C53.2, C54.1, C55.2, C56.1, C57.2, C58.1, C59.2, C60.1, C61.2, C62.1, C63.2, C65.2, C67.2, C69.1, D2.1, J5.1, J11.8, J16.3, J16.4, J17.2, J18.5, J18.6, J32.2, Q1.2, R1.2, R30.1, R36.1, R45.2, R48.2, R50.2, U1.1, U1.5, U1.6, U1.7, U1.8, U2.1, U2.5, U2.6, U2.7, U2.8, U3.8, U4.8, U5.3, U6.3, U7.3, U8.3, U9.1, U12.3, U12.10, U12.12, U15.3, U15.10, U15.12, U16.8, U16.21, U16.39, U16.41, U17.4, U18.2, U18.4, U20.3, Y1.2, Y1.4
MISO: J11.3, R49.1
MOSI: J11.4, U16.14
unnamed: C1.1, D1.2, J1.2, L1.1
unnamed: C9.1, U3.4, U4.4
unnamed: C12.2, J4.1
unnamed: C14.1, U5.1, U5.6
unnamed: C15.1, U6.1, U6.6
unnamed: C16.1, U7.1, U7.6
unnamed: C17.1, U8.1, U8.6
unnamed: C18.1, U9.5
unnamed: C19.1, R7.2, U9.2, U9.6
unnamed: C20.1, J6.1, R15.2, U10.3
unnamed: C20.3, J7.3, R14.2, U10.5
unnamed: C21.1, J9.1, R23.2, U13.3
unnamed: C21.3, J10.3, R22.2, U13.5
unnamed: C22.1, C23.1, U16.7
unnamed: C24.1, U16.12, Y1.1
unnamed: C25.1, U16.13, Y1.3
unnamed: C26.1, J6.3, R17.1, U10.1
unnamed: C26.2, R16.1, R17.2, U10.2
unnamed: C27.1, J7.1, R18.2, U10.7
unnamed: C27.2, R16.2, R18.1, U10.6
unnamed: C30.1, R20.2, U12.2
unnamed: C30.2, U11.6, U12.1
unnamed: C31.1, C32.1, U16.22
unnamed: C33.1, J9.3, R25.1, U13.1
unnamed: C33.2, R24.1, R25.2, U13.2
unnamed: C34.1, J10.1, R26.2, U13.7
unnamed: C34.2, R24.2, R26.1, U13.6
unnamed: C37.1, R28.2, U15.2
unnamed: C37.2, U14.6, U15.1
unnamed: C38.1, R21.2, R31.2, U12.5
unnamed: C39.1, R33.2, U12.13
unnamed: C39.2, R31.1, U12.14
unnamed: C40.1, J12.1, R32.1, R33.1, R34.2, U12.7
unnamed: C40.2, R30.2, R32.2, U12.6
unnamed: C43.1, R29.2, R37.2, U15.5
unnamed: C44.1, R39.2, U15.13
unnamed: C44.2, R37.1, U15.14
unnamed: C45.1, J14.1, R38.1, R39.1, R40.2, U15.7
unnamed: C45.2, R36.2, R38.2, U15.6
unnamed: C48.1, C49.1, U16.40, U17.6
unnamed: C50.1, C51.1, L2.1, U17.2
unnamed: C64.1, U18.6
unnamed: C64.2, U18.3
unnamed: C65.1, JP1.3, U18.5, U19.1
unnamed: C66.1, U19.6
unnamed: C66.2, U19.3
unnamed: C67.1, JP1.1, U19.5
unnamed: C68.1, U20.2
unnamed: C68.2, U20.4
unnamed: D1.1, R1.1
unnamed: D2.2, R44.2
unnamed: J3.1, R8.2, U9.3
unnamed: J3.3, Q1.3, R9.2
unnamed: J10.2, J14.3, U14.4
unnamed: J11.10, J34.2
unnamed: J11.12, R44.1
unnamed: J7.2, J12.3, U11.4
unnamed: J6.2, J13.1, U11.1
unnamed: J13.3, R35.1, U12.8
unnamed: J9.2, J15.1, U14.1
unnamed: J15.3, R41.1, U15.8
unnamed: J17.1, J19.1
unnamed: J18.1, J19.3
unnamed: JP2.2, U20.8
unnamed: R6.2, R7.1, U9.7
unnamed: R19.1, U11.3
unnamed: R19.2, U11.2
unnamed: R20.1, R21.1, U11.7
unnamed: R27.1, U14.3
unnamed: R27.2, U14.2
unnamed: R28.1, R29.1, U14.7
unnamed: R34.1, R35.2, U12.9
unnamed: R40.1, R41.2, U15.9
unnamed: R43.1, U16.19
RxI: J11.2, J32.4
SCL: J11.5, R46.1
TxO: J11.1, J32.3
VCC: J32.1, J34.1
VCCIO: C7.1, C8.1, J2.2, J24.2, U3.3, U4.3

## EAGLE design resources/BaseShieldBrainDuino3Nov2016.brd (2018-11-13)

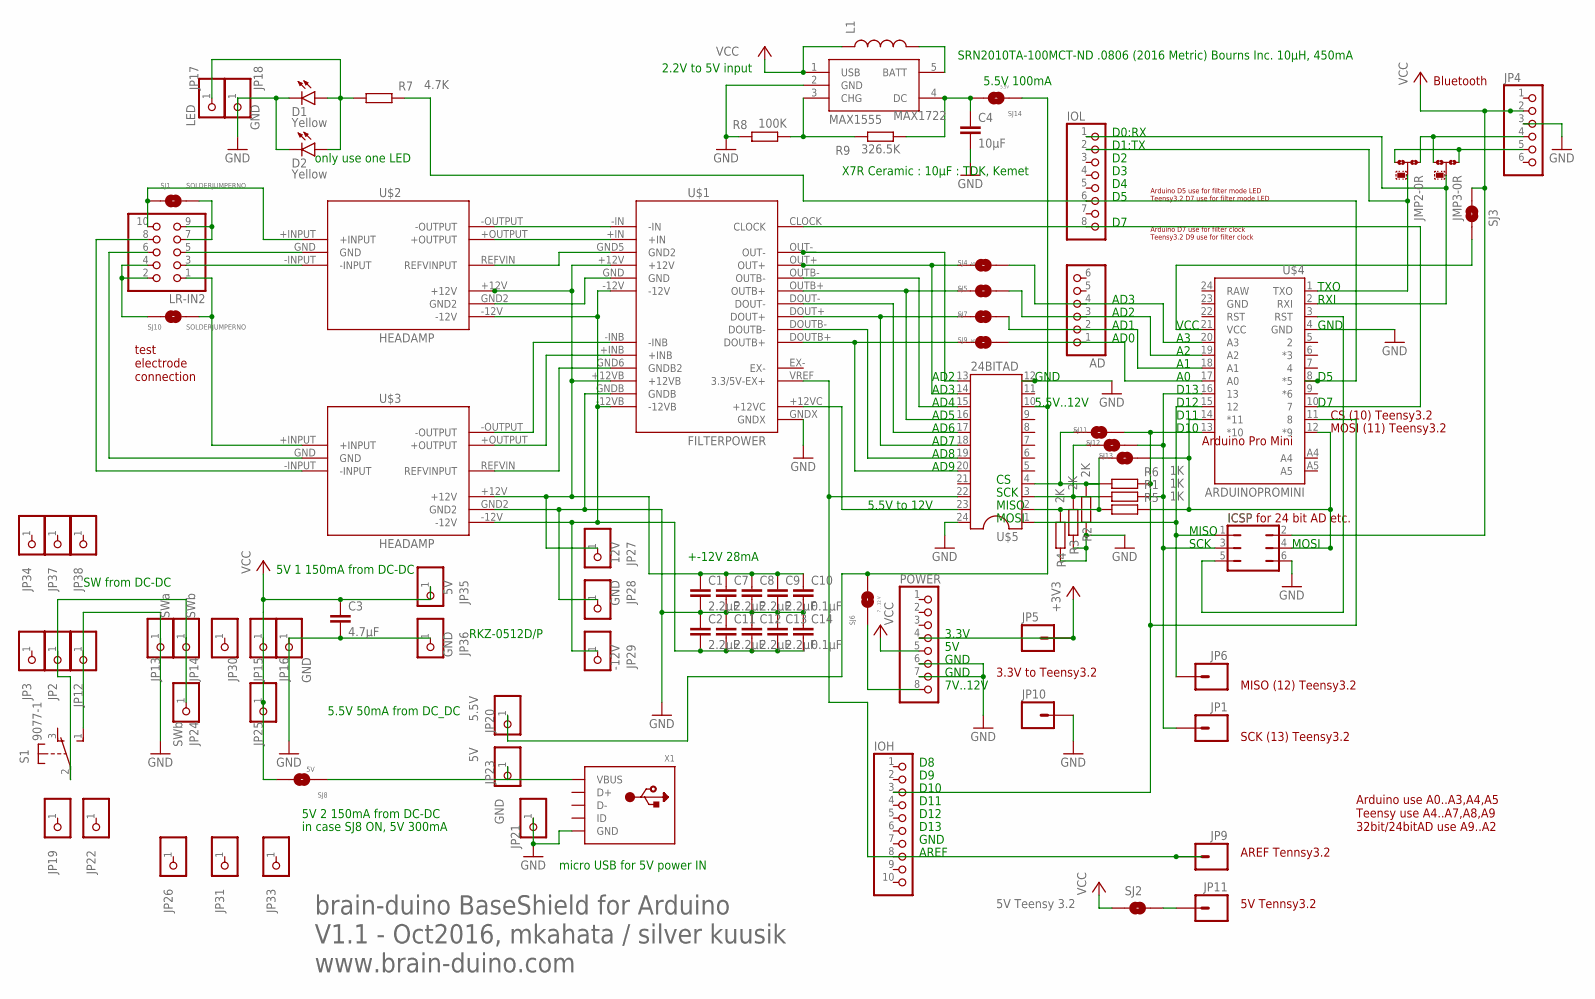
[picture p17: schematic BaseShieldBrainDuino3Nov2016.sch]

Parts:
AD: PINHD-1X6; 1X06
C1, C2, C7, C8, C9, C11, C12, C13: 2.2µF; C0402
C3: 4.7µF; C0402
C4: 10µF; C0402
C10, C14: 0.1µF; C0402
D1, D2: Yellow; LED-0603
ICSP: JP3Q
IOH: PINHD-1X10; 1X10
IOL: PINHD-1X8; 1X08
JMP2: RX; A0R-JMP
JMP3: TX; A0R-JMP
JP1, JP5, JP6, JP9, JP10, JP11: M01PTH; 1X01
JP2, JP3, JP12, JP19, JP22, JP26, JP30, JP31, JP33, JP34, JP37, JP38: PINHD-1X1; 1X01
JP4: PINHD-1X6; 1X06
JP13: SWa; 1X01
JP14, JP24: SWb; 1X01
JP15, JP25: +5V; 1X01
JP16, JP18, JP21, JP28, JP36: GND; 1X01
JP17: LED; 1X01
JP20: 5.5V; 1X01
JP23, JP35: 5V; 1X01
JP27: 12V; 1X01
JP29: -12V; 1X01
L1: INDUCTOR0805; 0805
LR-IN2: PINHD-2X5/90; 2X05/90
MAX1722: MAX1555; SOT23-5
POWER: PINHD-1X8; 1X08
R1, R5, R6: 1K; R0402
R2, R3, R4: 2K; R0402
R7: 4.7K; R0402
R8: 100K; R0402
R9: 326.5K; R0402
S1: 9077-1
SJ1, SJ10: SOLDERJUMPERNO; SJ_2S-NO
SJ2: 5V Teensy 3.2; SJ_2S-NO
SJ3: 5V Arduino Pro Mini; SJ_2S-NO
SJ4: A5; SJ_2S-NO
SJ5, SJ11, SJ12, SJ13: A4; SJ_2S-NO
SJ6: 7 .. 12 V; SJ_2S-NO
SJ7: A2; SJ_2S-NO
SJ8: 5V; SJ_2S-NO
SJ9: A0; SJ_2S-NO
SJ14: 5.5V; SJ_2S-NO
U$1: FILTERPOWER
U$2, U$3: HEADAMP
U$4: ARDUINOPROMINI
U$5: 24BITAD
X1: USB_MICRO_20329_V2; 4UCONN_20329_V2

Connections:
+3V3: JP5.1, POWER.4
+12VB: C1.1, C7.1, C8.1, C9.1, C10.1, JP27.1, U$1.+12V, U$1.+12VB, U$2.+12V, U$3.+12V
-12V: C2.2, C11.2, C12.2, C13.2, C14.2, JP29.1, U$1.-12V, U$1.-12VB, U$2.-12V, U$3.-12V
GND: C1.2, C2.1, C3.2, C4.2, C7.2, C8.2, C9.2, C10.2, C11.1, C12.1, C13.1, C14.1, D1.C, D2.C, ICSP.6, JP4.3, JP10.1, JP12.1, JP13.1, JP16.1, JP18.1, JP21.1, JP28.1, JP36.1, MAX1722.2 (GND), POWER.6, POWER.7, R2.1, R3.1, R4.1, R8.1, S1.1 (S), U$1.GNDB, U$1.GNDX, U$3.GND2, U$4.4 (GND), U$5.12, U$5.24, X1.BASE@1 (GND), X1.BASE@2 (GND), X1.GND, X1.SPRT@1 (GND), X1.SPRT@2 (GND), X1.SPRT@3 (GND), X1.SPRT@4 (GND)
unnamed: SJ3.1, U$4.21 (VCC)
unnamed: U$1.GND, U$2.GND2
unnamed: JP2.1, JP14.1, JP24.1, S1.2
unnamed: POWER.8, SJ6.1
unnamed: ICSP.3, JP1.1, R1.2, SJ12.2, U$4.16 (13)
unnamed: LR-IN2.8, U$3.-INPUT
unnamed: JP23.1, SJ8.1, X1.VBUS
unnamed: U$1.GND6 (GNDB2), U$3.REFVIN (REFVINPUT)
unnamed: U$1.-INB, U$3.-OUTPUT
unnamed: U$1.+INB, U$3.+OUTPUT
unnamed: LR-IN2.3, U$2.-INPUT
unnamed: U$1.OUTB-, U$5.15
unnamed: U$1.+12VC, U$5.23
unnamed: U$1.OUT-, U$5.13
unnamed: JMP2.1, JMP3.3, JP4.4
unnamed: IOL.8, U$1.CLOCK, U$4.10 (7)
unnamed: ICSP.1, JP6.1, U$4.15 (12), U$5.1
unnamed: IOL.2, JMP2.2, U$4.1 (TXO)
unnamed: U$1.-IN, U$2.-OUTPUT
unnamed: IOL.1, JMP3.2, U$4.2 (RXI)
unnamed: IOH.3, R6.2, SJ11.2, U$4.11 (8), U$4.13 (*10)
unnamed: AD.2, SJ7.2, U$4.18 (A1)
unnamed: AD.1, SJ9.2, U$4.17 (A0)
unnamed: ICSP.4, R5.2, SJ13.2, U$4.12 (*9), U$4.14 (*11)
unnamed: JMP2.3, JMP3.1, JP4.5
unnamed: SJ9.1, U$1.DOUTB+, U$5.20
unnamed: JP11.1, SJ2.2
unnamed: JP20.1, SJ6.2, SJ14.1, U$5.10
unnamed: U$1.DOUTB-, U$5.19
unnamed: U$1.+IN, U$2.+OUTPUT
unnamed: SJ7.1, U$1.DOUT+, U$5.18
unnamed: U$1.DOUT-, U$5.17
unnamed: IOH.8, JP9.1, U$1.VREF (3.3/5V-EX+), U$5.22
unnamed: AD.4, SJ4.2, U$4.20 (A3)
unnamed: C4.1, MAX1722.4 (DC), R9.2, SJ14.2
unnamed: SJ4.1, U$1.OUT+, U$5.14
unnamed: SJ5.1, U$1.OUTB+, U$5.16
unnamed: LR-IN2.1, SJ10.2, U$3.+INPUT
unnamed: LR-IN2.10, SJ1.1, U$2.+INPUT
unnamed: LR-IN2.7, LR-IN2.9, SJ1.2
unnamed: LR-IN2.2, LR-IN2.4, SJ10.1
unnamed: R2.2, R6.1, SJ11.1, U$5.4
unnamed: R1.1, R3.2, SJ12.1, U$5.3
unnamed: R4.2, R5.1, SJ13.1, U$5.2
unnamed: AD.3, SJ5.2, U$4.19 (A2)
unnamed: U$1.GND5 (GND2), U$2.REFVIN (REFVINPUT)
unnamed: L1.2, MAX1722.5 (BATT)
unnamed: LR-IN2.6, U$3.GND
unnamed: MAX1722.3 (CHG), R8.2, R9.1
unnamed: ICSP.5, U$4.3 (RST)
unnamed: D1.A, D2.A, JP17.1, R7.1
unnamed: IOL.6, R7.2, U$4.8 (*5)
unnamed: LR-IN2.5, U$2.GND
VCC: C3.1, ICSP.2, JP4.2, JP15.1, JP25.1, JP35.1, L1.1, MAX1722.1 (USB), POWER.5, SJ2.1, SJ3.2, SJ8.2

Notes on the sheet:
D0:RX
D1:TX
D13
D12
AREF
GND
AD0
AD1
AD2
AD3
7V..12V
D10
D11
test electrode connection
MOSI (11) Teensy3.2
brain-duino BaseShield for Arduino V1.1 - Oct2016, mkahata / silver kuusik www.brain-duino.com
Bluetooth
MOSI
MISO
SCK
3.3V to Teensy3.2
SCK (13) Teensy3.2
MISO (12) Teensy3.2
ICSP for 24 bit AD etc.
CS (10) Teensy3.2
Arduino use A0..A3,A4,A5 Teensy use A4..A7,A8,A9 32bit/24bitAD use A9..A2
5V Tennsy3.2
Arduino D7 use for filter clock Teensy3.2 D9 use for filter clock
3.3V
AD9
AD8
AD7
AD6
AD5
AD4
5.5V..12V
AREF Tennsy3.2
TXO
RXI
VCC

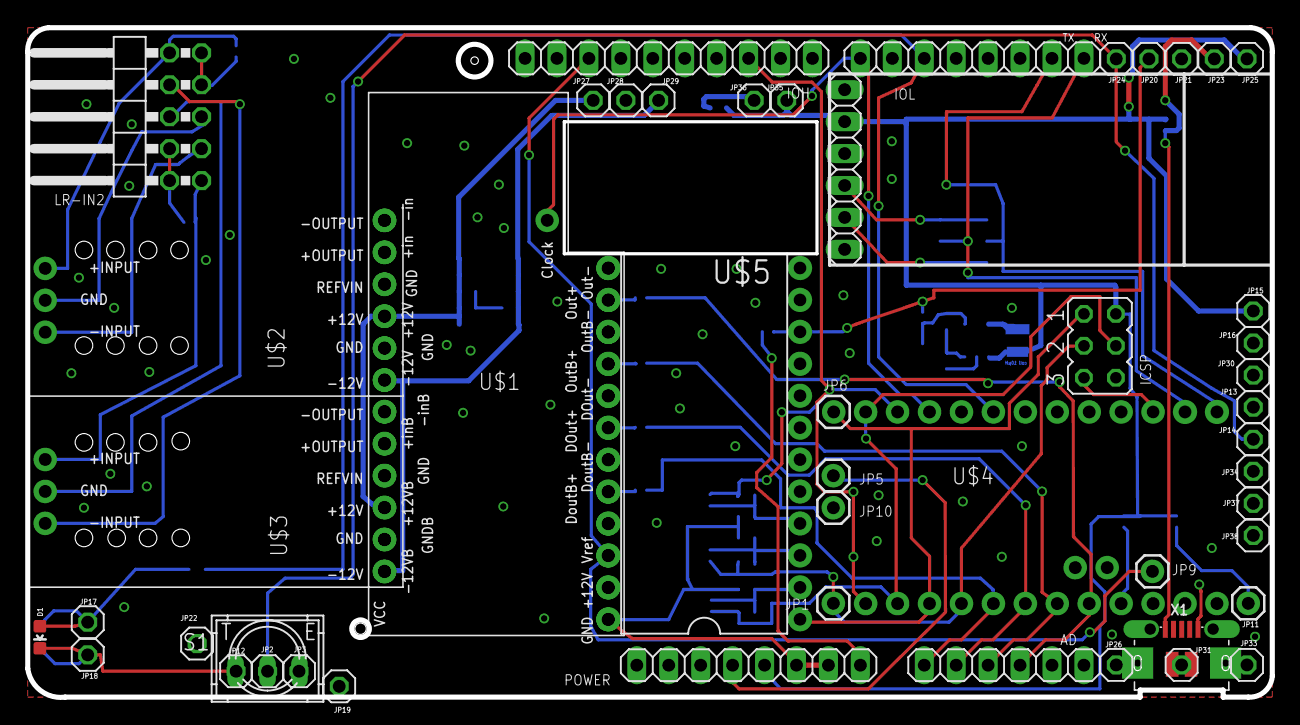
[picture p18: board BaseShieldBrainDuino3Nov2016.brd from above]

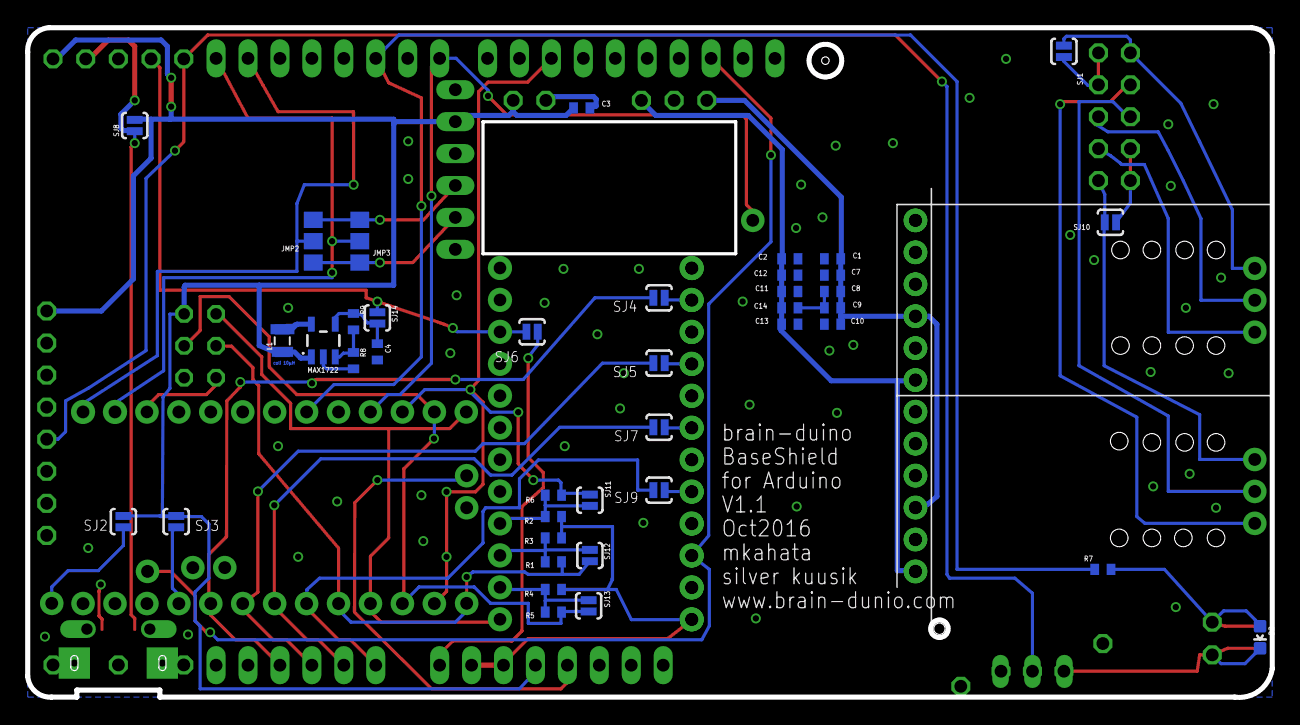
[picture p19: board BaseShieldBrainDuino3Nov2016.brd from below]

Board: 2 copper layers, 99.0 x 53.3 mm, 89 parts (40 on the bottom side), 58 nets.

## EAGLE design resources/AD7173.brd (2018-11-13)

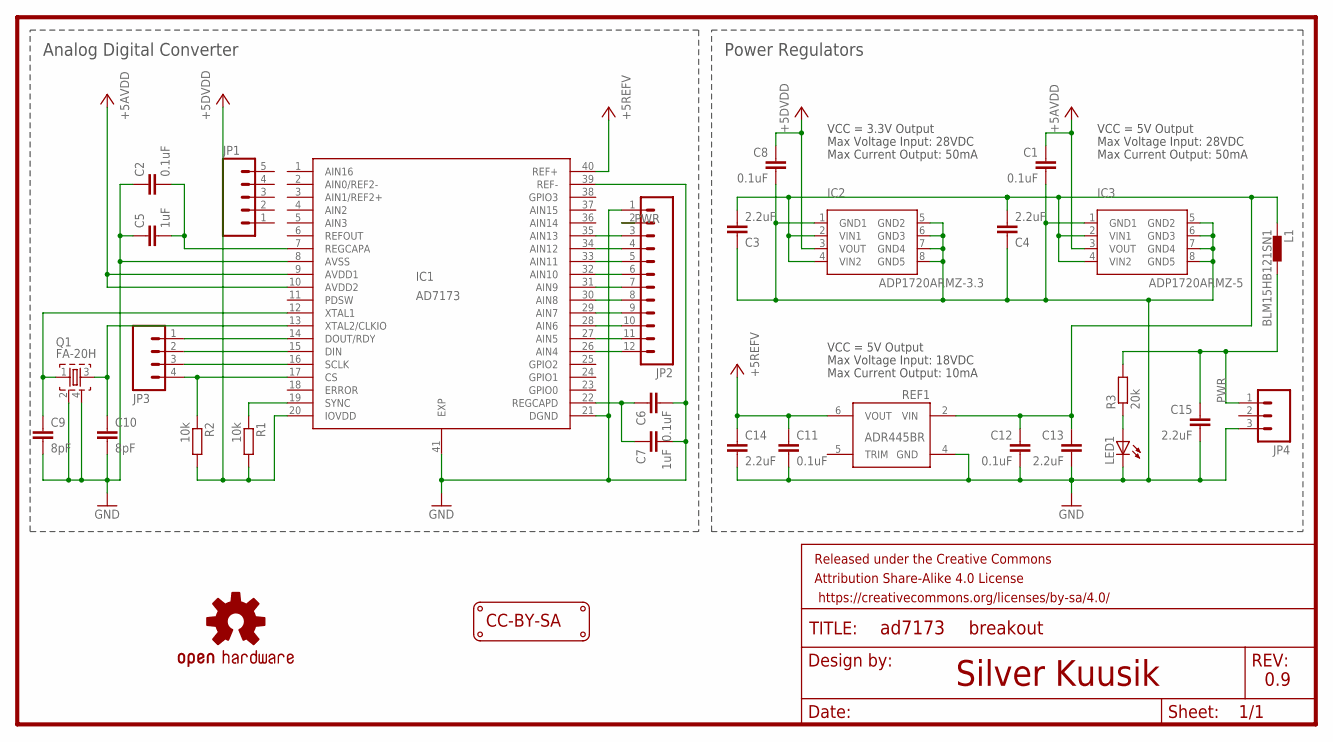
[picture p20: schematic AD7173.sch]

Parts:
C1, C2, C6, C8, C11, C12: 0.1uF; C0402
C3, C4, C13, C14, C15: 2.2uF; C0402
C5, C7: 1uF; C0402
C9, C10: 8pF; C0402
FRAME1: FRAME-LETTER; CREATIVE_COMMONS
IC1: AD7173; LFCSP_WQ6X6MM
IC2: ADP1720ARMZ-3.3; MSOP08
IC3: ADP1720ARMZ-5; MSOP08
JP1: M05PTH; 1X05
JP2: M12PTH; 1X12
JP3: M04PTH; 1X04
JP4: M03PTH; 1X03
L1: BLM15HB121SN1; 0402
LED1: LEDCHIP-LED0603; CHIP-LED0603
LOGO1: OSHW-LOGOS; OSHW-LOGO-S
LOGO2: LOGO_CC-BY-SA
Q1: FA-20H
R1, R2: 10k; R0402
R3: 20k; R0402
REF1: ADR445BR; SO8

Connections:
+3V3: C8.1, IC1.20 (IOVDD), IC2.3 (VOUT), R1.2, R2.2
+5V: C1.1, IC1.9 (AVDD1), IC1.10 (AVDD2), IC3.3 (VOUT)
GND: C1.2, C2.1, C3.1, C4.1, C5.1, C6.2, C7.2, C8.2, C9.2, C10.2, C11.2, C12.2, C13.2, C14.2, C15.2, IC1.8 (AVSS), IC1.21 (DGND), IC1.39 (REF-), IC1.41 (EXP), IC2.1 (GND1), IC2.5 (GND2), IC2.6 (GND3), IC2.7 (GND4), IC2.8 (GND5), IC3.1 (GND1), IC3.5 (GND2), IC3.6 (GND3), IC3.7 (GND4), IC3.8 (GND5), JP2.1, JP4.3, LED1.C, Q1.2, Q1.4, REF1.4 (GND)
unnamed: IC1.16 (SCLK), JP3.3
unnamed: IC1.17 (CS), JP3.4, R2.1
unnamed: C6.1, C7.1, IC1.22 (REGCAPD)
unnamed: IC1.34 (AIN12), JP2.4
unnamed: C2.2, C5.2, IC1.7 (REGCAPA)
unnamed: IC1.35 (AIN13), JP2.3
unnamed: IC1.33 (AIN11), JP2.5
unnamed: IC1.32 (AIN10), JP2.6
unnamed: IC1.31 (AIN9), JP2.7
unnamed: IC1.30 (AIN8), JP2.8
unnamed: IC1.29 (AIN7), JP2.9
unnamed: IC1.15 (DIN), JP3.2
unnamed: IC1.27 (AIN5), JP2.11
unnamed: IC1.26 (AIN4), JP2.12
unnamed: C10.1, IC1.13 (XTAL2/CLKIO), Q1.3
unnamed: IC1.28 (AIN6), JP2.10
unnamed: IC1.14 (DOUT/RDY), JP3.1
unnamed: C9.1, IC1.12 (XTAL1), Q1.1
unnamed: LED1.A, R3.1
unnamed: IC1.19 (SYNC), R1.1
PWR: C15.1, JP2.2, JP4.1, L1.2, R3.2
VCC: C11.1, C14.1, IC1.40 (REF+), REF1.6 (VOUT)
VIN: C3.2, C4.2, C12.1, C13.1, IC2.2 (VIN1), IC2.4 (VIN2), IC3.2 (VIN1), IC3.4 (VIN2), L1.1, REF1.2 (VIN)

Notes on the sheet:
Power Regulators
Analog Digital Converter
VCC = 3.3V Output
Max Current Output: 50mA
Max Voltage Input: 28VDC
VCC = 5V Output
Max Voltage Input: 18VDC
Max Current Output: 10mA
Silver Kuusik
breakout
0.9

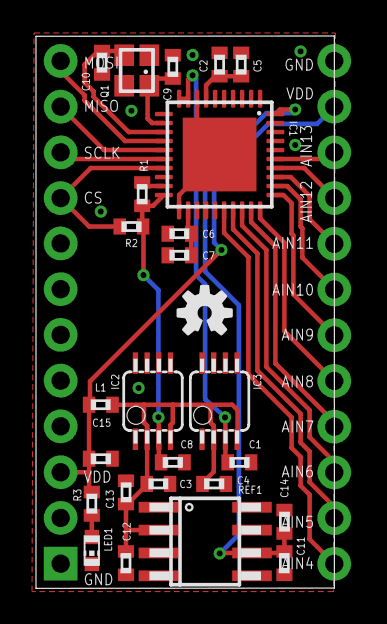
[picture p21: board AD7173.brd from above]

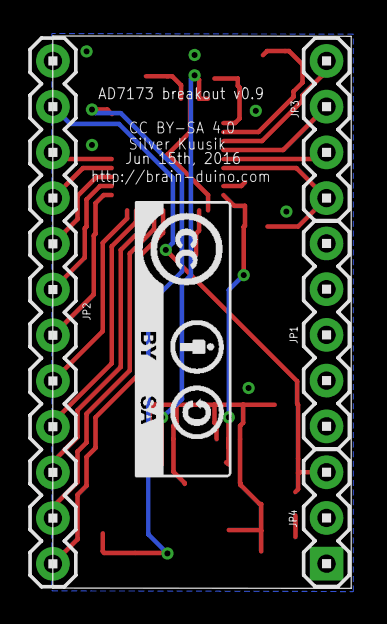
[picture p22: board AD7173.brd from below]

Board: 2 copper layers, 16.6 x 30.7 mm, 32 parts (5 on the bottom side), 26 nets.

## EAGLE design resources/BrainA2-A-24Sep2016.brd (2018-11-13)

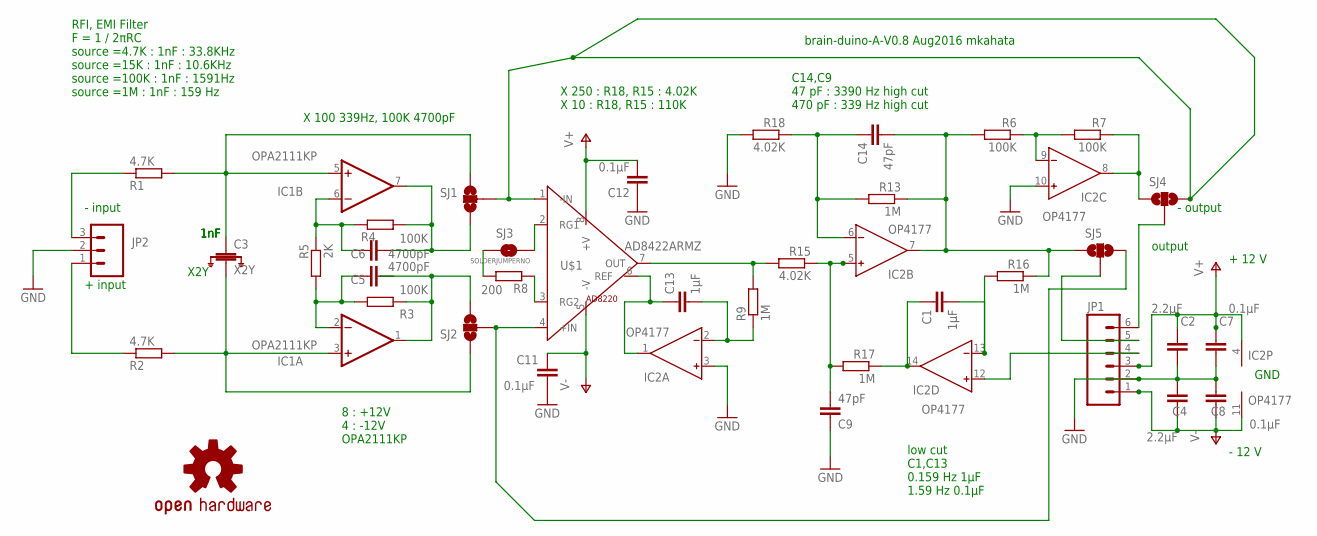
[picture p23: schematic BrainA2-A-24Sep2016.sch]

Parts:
C1, C13: 1µF; C0402
C2, C4: 2.2µF; C0402
C3: X2Y; C0603
C5, C6: 4700pF; C0402
C7, C8, C11, C12: 0.1µF; C0402
C9, C14: 47pF; C0402
IC1: OPA2111KP; DIL08
IC2: OP4177; TSSOP14
JP1: M06SILK_FEMALE_PTH; 1X06
JP2: M03PTH; 1X03
LOGO1: OSHW-LOGOS; OSHW-LOGO-S
R1, R2: 4.7K; R0402
R3, R4, R6, R7: 100K; R0402
R5: 2K; R0402
R8: 200; R0402
R9, R13, R16, R17: 1M; R0402
R15, R18: 4.02K; R0402
SJ1, SJ2, SJ4, SJ5: SOLDERJUMPER_2WAYPASTE2&3; SJ_3_PASTE2&3
SJ3: SOLDERJUMPERNO; SJ_2S-NO
U$1: AD8422ARMZ; AD8220

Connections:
GND: C2.1, C3.GND, C4.2, C7.1, C8.2, C9.1, C11.2, C12.1, IC2.3 (IN+), IC2.10 (IN+), JP1.2, JP2.2, R18.2
unnamed: JP2.3, R1.1
unnamed: R8.2, SJ3.1
unnamed: JP2.1, R2.1
unnamed: C3.2, IC1.3 (+IN), R2.2, SJ2.1
unnamed: C3.1, IC1.5 (+IN), R1.2, SJ1.1
unnamed: IC2.9 (IN-), R6.1, R7.2
unnamed: C5.1, IC1.2 (-IN), R3.1, R5.2
unnamed: C6.1, IC1.6 (-IN), R4.1, R5.1
unnamed: SJ1.2, SJ4.1, U$1.1 (-IN)
unnamed: SJ2.2, SJ5.1, U$1.4 (+IN)
unnamed: C5.2, IC1.1 (OUT), R3.2, SJ2.3
unnamed: C6.2, IC1.7 (OUT), R4.2, SJ1.3
unnamed: R8.1, U$1.3 (RG2)
unnamed: JP1.6, SJ4.2
unnamed: C1.2, IC2.13 (IN-), R16.2
unnamed: SJ3.2, U$1.2 (RG1)
unnamed: C9.2, IC2.5 (IN+), R15.1, R17.2
unnamed: R9.2, R15.2, U$1.7 (OUT)
unnamed: C13.2, IC2.2 (IN-), R9.1
unnamed: C14.2, IC2.7 (OUT), R6.2, R13.1, R16.1, SJ5.3
unnamed: C13.1, IC2.1 (OUT), U$1.6 (REF)
unnamed: C14.1, IC2.6 (IN-), R13.2, R18.1
unnamed: IC2.12 (IN+), JP1.4
unnamed: C1.1, IC2.14 (OUT), R17.1
unnamed: IC2.8 (OUT), R7.1, SJ4.3
unnamed: JP1.5, SJ5.2
V+: C2.2, C7.2, C12.2, IC1.8 (V+), IC2.4 (V+), JP1.3, U$1.8 (+V)
V-: C4.1, C8.1, C11.1, IC1.4 (V-), IC2.11 (V-), JP1.1, U$1.5 (-V)

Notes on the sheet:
+ 12 V
- 12 V
GND
brain-duino-A-V0.8 Aug2016 mkahata
X2Y
output
- output
8 : +12V 4 : -12V OPA2111KP
+ input
- input
1nF
X 100 339Hz, 100K 4700pF
X 250 : R18, R15 : 4.02K X 10 : R18, R15 : 110K
RFI, EMI Filter F = 1 / 2πRC source =4.7K : 1nF : 33.8KHz source =15K : 1nF : 10.6KHz source =100K : 1nF : 1591Hz source =1M : 1nF : 159 Hz
low cut C1,C13 0.159 Hz 1µF 1.59 Hz 0.1µF
C14,C9 47 pF : 3390 Hz high cut 470 pF : 339 Hz high cut

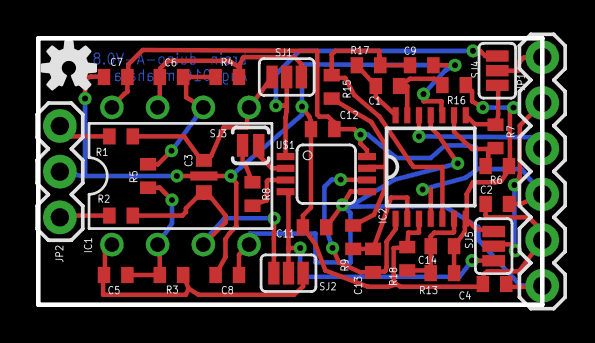
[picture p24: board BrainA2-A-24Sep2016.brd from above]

Board: 2 copper layers, 28.0 x 14.8 mm, 38 parts (0 on the bottom side), 29 nets.

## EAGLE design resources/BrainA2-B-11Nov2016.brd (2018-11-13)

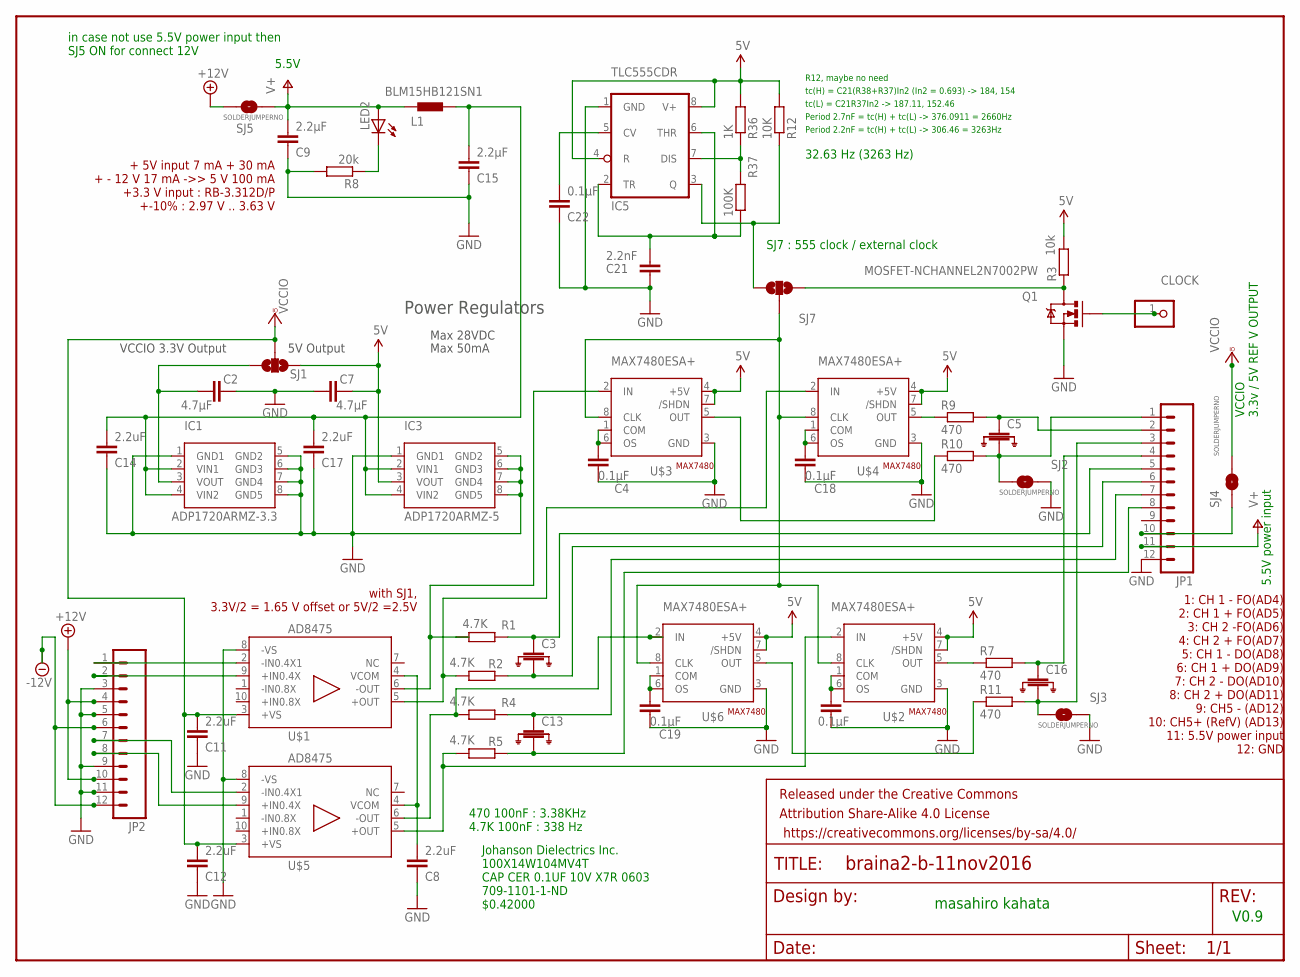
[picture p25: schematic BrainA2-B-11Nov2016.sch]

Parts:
C1, C4, C18, C19: 0.1µF; 0402-CAP
C2, C7: 4.7µF; 0402-CAP
C3, C5, C13, C16: C-EUX2Y; C0603
C8, C11, C12, C14, C17: 2.2uF; C0402
C9, C15: 2.2µF; 0402-CAP
C21: 2.2nF; C0402
C22: 0.1µF; C0402
CLOCK: PINHD-1X1; 1X01
FRAME1: FRAME-LETTER; CREATIVE_COMMONS
IC1: ADP1720ARMZ-3.3; MSOP08
IC3: ADP1720ARMZ-5; MSOP08
IC5: TLC555CDR; SO08
JP1, JP2: M12NO_SILK; 1X12_NO_SILK
L1: BLM15HB121SN1; 0402
LED2: LEDCHIP-LED0603; CHIP-LED0603
Q1: MOSFET-NCHANNEL2N7002PW; SOT323
R1, R2, R4, R5: 4.7K; R0402
R3: 10k; R0402
R7, R9, R10, R11: 470; R0402
R8: 20k; R0402
R12: 10K; R0402
R36: 1K; R0402
R37: 100K; R0402
SJ1, SJ7: SOLDERJUMPER_2WAYS; SJ_3
SJ2, SJ3, SJ4, SJ5: SOLDERJUMPERNO; SJ_2S-NO
U$1, U$5: AD8475; MSOP10
U$2, U$3, U$4, U$6: MAX7480ESA+; MAX7480

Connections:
5V: C7.1, IC3.3 (VOUT), IC5.4 (R), IC5.8 (V+), R3.2, R12.2, R36.2, SJ1.1, U$2.4 (+5V), U$2.7 (/SHDN), U$3.4 (+5V), U$3.7 (/SHDN), U$4.4 (+5V), U$4.7 (/SHDN), U$6.4 (+5V), U$6.7 (/SHDN)
+12V: JP2.4, JP2.10, SJ5.1
-12V: JP2.6, JP2.12
GND: C1.1, C2.1, C3.GND, C4.1, C5.GND, C7.2, C8.1, C9.1, C11.1, C12.1, C13.GND, C14.1, C15.1, C16.GND, C17.1, C18.1, C19.1, C21.1, C22.1, IC1.1 (GND1), IC1.5 (GND2), IC1.6 (GND3), IC1.7 (GND4), IC1.8 (GND5), IC3.1 (GND1), IC3.5 (GND2), IC3.6 (GND3), IC3.7 (GND4), IC3.8 (GND5), IC5.1 (GND), JP1.12, JP2.3, JP2.5, JP2.9, JP2.11, Q1.2 (S), R8.2, SJ2.2, SJ3.2, U$1.8 (-VS), U$2.3 (GND), U$3.3 (GND), U$4.3 (GND), U$5.8 (-VS), U$6.3 (GND)
unnamed: C13.2, JP1.8, R5.2
unnamed: C1.2, U$2.1 (COM), U$2.6 (OS)
unnamed: R11.1, U$6.5 (OUT)
unnamed: JP2.1, U$1.2 (-IN0.4X1)
unnamed: R7.1, U$2.5 (OUT)
unnamed: JP2.2, U$1.9 (+IN0.4X)
unnamed: C3.2, JP1.6, R2.2
unnamed: C3.1, JP1.5, R1.2
unnamed: C5.2, JP1.1, R10.2, SJ2.1
unnamed: R2.1, U$1.5 (+OUT), U$4.2 (IN)
unnamed: C4.2, U$3.1 (COM), U$3.6 (OS)
unnamed: Q1.3 (D), R3.1, SJ7.3
unnamed: JP1.10, SJ4.1
unnamed: R10.1, U$3.5 (OUT)
unnamed: C8.2, U$1.4 (VCOM), U$5.4 (VCOM)
unnamed: LED2.C, R8.1
unnamed: R4.1, U$5.6 (-OUT), U$6.2 (IN)
unnamed: JP2.8, U$5.9 (+IN0.4X)
unnamed: C13.1, JP1.7, R4.2
unnamed: JP2.7, U$5.2 (-IN0.4X1)
unnamed: C5.1, JP1.2, R9.2
unnamed: C18.2, U$4.1 (COM), U$4.6 (OS)
unnamed: C14.2, C15.2, C17.2, IC1.2 (VIN1), IC1.4 (VIN2), IC3.2 (VIN1), IC3.4 (VIN2), L1.2
unnamed: R9.1, U$4.5 (OUT)
unnamed: CLOCK.1, Q1.1 (G)
unnamed: R5.1, U$2.2 (IN), U$5.5 (+OUT)
unnamed: R1.1, U$1.6 (-OUT), U$3.2 (IN)
unnamed: IC5.3 (Q), R12.1, SJ7.1
unnamed: C16.1, JP1.4, R7.2
unnamed: C2.2, IC1.3 (VOUT), SJ1.3
unnamed: C16.2, JP1.3, R11.2, SJ3.1
unnamed: C19.2, U$6.1 (COM), U$6.6 (OS)
unnamed: SJ7.2, U$2.8 (CLK), U$3.8 (CLK), U$4.8 (CLK), U$6.8 (CLK)
unnamed: IC5.7 (DIS), R36.1, R37.2
unnamed: C21.2, IC5.2 (TR), IC5.6 (THR), R37.1
unnamed: C22.2, IC5.5 (CV)
V+: C9.2, JP1.11, L1.1, LED2.A, SJ5.2
VCCIO: C11.2, C12.2, SJ1.2, SJ4.2, U$1.3 (+VS), U$5.3 (+VS)

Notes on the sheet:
+ 5V input 7 mA + 30 mA + - 12 V 17 mA ->> 5 V 100 mA +3.3 V input : RB-3.312D/P +-10% : 2.97 V .. 3.63 V
masahiro kahata
1: CH 1 - FO(AD4) 2: CH 1 + FO(AD5) 3: CH 2 -FO(AD6) 4: CH 2 + FO(AD7) 5: CH 1 - DO(AD8) 6: CH 1 + DO(AD9) 7: CH 2 - DO(AD10) 8: CH 2 + DO(AD11) 9: CH5 - (AD12) 10: CH5+ (RefV) (AD13) 11: 5.5V power input 12: GND
with SJ1, 3.3V/2 = 1.65 V offset or 5V/2 =2.5V
VCCIO 3.3v / 5V REF V OUTPUT
32.63 Hz (3263 Hz)
SJ7 : 555 clock / external clock
5.5V power input
470 100nF : 3.38KHz 4.7K 100nF : 338 Hz
Johanson Dielectrics Inc. 100X14W104MV4T CAP CER 0.1UF 10V X7R 0603 709-1101-1-ND $0.42000
V0.9
Power Regulators
VCCIO 3.3V Output
5V Output
Max 50mA
Max 28VDC
R12, maybe no need
tc(H) = C21(R38+R37)In2 (In2 = 0.693) -> 184, 154
tc(L) = C21R37In2 -> 187.11, 152.46
Period 2.7nF = tc(H) + tc(L) -> 376.0911 = 2660Hz
Period 2.2nF = tc(H) + tc(L) -> 306.46 = 3263Hz
5.5V
in case not use 5.5V power input then SJ5 ON for connect 12V

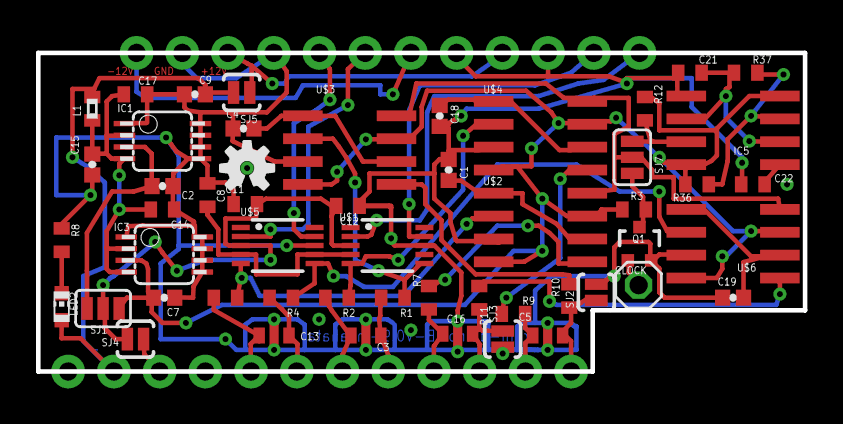
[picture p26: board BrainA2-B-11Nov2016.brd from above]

Board: 2 copper layers, 42.6 x 17.7 mm, 55 parts (0 on the bottom side), 42 nets.

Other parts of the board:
U$8: OSHW-LOGO-S

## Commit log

2014-05-13 AD7173.ino added get current adc data channel
2014-05-17 schematics/* added eagle schematics files for the ADC
    [AD7173.brd, AD7173.sch]
2014-05-22 AD7173/* create arduino library, renamed schematics
    [AD7173.brd, AD7173.sch]
2014-06-12 circuits/* updated eagle circuits
    [AD7173.brd, AD7173.sch]
2014-07-26 circuits/AD7173/* moved AD7173 circuit to it's own folder
    [AD7173.brd, AD7173.sch]
2014-07-26 circuits/amplifier/* added amplifier circuit
    [amplifier.brd, amplifier.sch]
2015-03-18 updated aplifier circuit
    [amplifier.brd, amplifier.sch]
2015-04-11 added ADC test code for raspberry pi
2015-04-11 upadted AD7173 circuits
    [AD7173.brd, AD7173.sch]
2015-04-11 upadted raspberry pi code
2015-06-27 updated AD7173 circuit
    [AD7173.brd, AD7173.sch]
2015-06-28 updated AD7173 breakout board
    [AD7173.brd, AD7173.sch]
2015-07-03 upadted AD7173 breakout board
    [AD7173.brd, AD7173.sch]
2015-08-20 updated raspberry pi library
2015-09-03 updated pins, components placing
    [AD7173.brd, AD7173.sch]
2015-09-05 small margin updates
    [AD7173.brd]
2015-09-05 updated label
    [AD7173.brd]
2018-11-13 init: updated repo with new layouts
    [AD7173.brd, AD7173.sch, Amplifier.sch, Attenuator.sch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]
2018-11-14 refactor: reordered folder structure
    [AD7173.brd, AD7173.sch, Amplifier.sch, Attenuator.sch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]
2018-11-17 updated schematics
    [Attenuator.sch, ExternalPower.sch, MAX7480Block.sch, PowerRegulator.sch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]
2018-11-18 added ADC Chip
    [ADConverter.sch, Amplifier.sch, Attenuator.sch, ClockBlock.sch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]
2018-11-20 added arduino base
    [ADConverter.sch, Amplifier.sch, Attenuator.sch, CapBank.sch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]
2018-11-21 added footprints
    [ADConverter.sch, Amplifier.sch, Attenuator.sch, CapBank.sch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]
2018-11-21 complete schematics
    [ADConverter.sch, Amplifier.sch, SPIConnector.sch, USBPower.sch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]
2018-11-21 added decouple capacitors
    [Amplifier.sch, RCFilterBlock1.sch, RCFilterBlock2.sch, neurolab.kicad_pcb]
2018-11-24 pcb layout for amplifier block
    [RCFilterBlock1.sch, SPIConnector.sch, USBPower.sch, neurolab.kicad_pcb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]
2018-11-24 feat: power circuitry
    [Amplifier.sch, USBPower.sch, neurolab.kicad_pcb, neurolab.sch]
2018-11-26 feat: attenuator and clock circuits
    [neurolab.kicad_pcb]
2018-11-27 feat: filter circuits
    refactor
    [ADConverter.sch, MAX7480Block.sch, neurolab.kicad_pcb]
2018-11-28 feat: ADC Circuit
    [neurolab.kicad_pcb, neurolab.sch]
2018-11-29 refactor: route improvements
    [neurolab.kicad_pcb, neurolab.sch]
2018-11-29 docs: added BoM
    [NeuroLab_BOM_Sheet.ods]
2018-12-01 optimize: routing and placement
    optimize: squeeze space
    optimize: squeeze space contd.
    optimize: contd.
    [Amplifier.sch, RCFilterBlock1.sch, SPIConnector.sch, USBPower.sch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]
2018-12-03 optimize: component placement
    [neurolab.kicad_pcb]
2018-12-03 optimize: reduce spacing 20mils
    [neurolab.kicad_pcb]
2018-12-03 optimize: redundant foot prints
    [neurolab.kicad_pcb, neurolab.sch]
2018-12-03 optimize: routing to minimize length
    [ADConverter.sch, neurolab.kicad_pcb]
2018-12-03 optimize: alternative route for +5V
    [neurolab.kicad_pcb]
2018-12-03 optimize: route parts
    [ADConverter.sch, neurolab.kicad_pcb]
2018-12-03 optimize: removed redundant SPI connector
    [SPIConnector.sch, neurolab.kicad_pcb]
2018-12-03 optimize: routing SPI
    [neurolab.kicad_pcb, neurolab.sch]
2018-12-04 optimize: final routing
    [Amplifier.sch, neurolab.kicad_pcb, neurolab.sch]
2019-03-26 feat: schematics and readme update
    [ADConverter-2019-03-07-23-26-57.sch, ADConverter.sch, Amplifier-2019-03-07-23-26-57.sch, Amplifier.sch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]

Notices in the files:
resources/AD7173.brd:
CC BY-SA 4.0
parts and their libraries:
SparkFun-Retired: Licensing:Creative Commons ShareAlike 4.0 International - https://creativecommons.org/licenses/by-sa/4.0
